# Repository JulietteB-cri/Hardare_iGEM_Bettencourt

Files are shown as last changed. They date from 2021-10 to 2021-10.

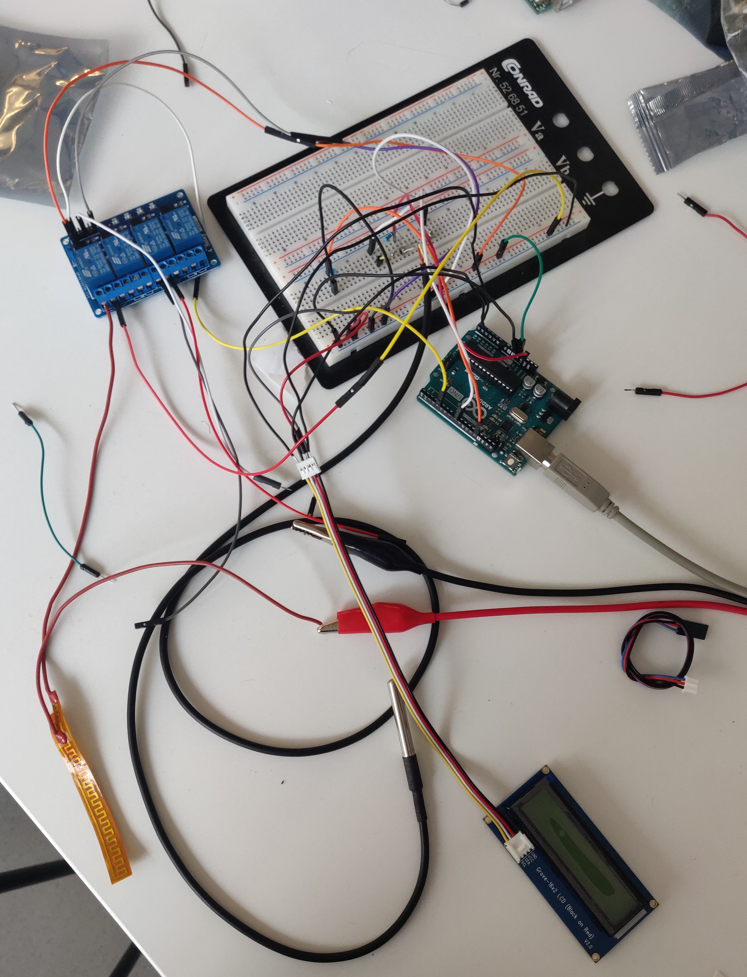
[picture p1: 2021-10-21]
Pictures/Firsts Drafts/IMG_20210827_180004.jpg

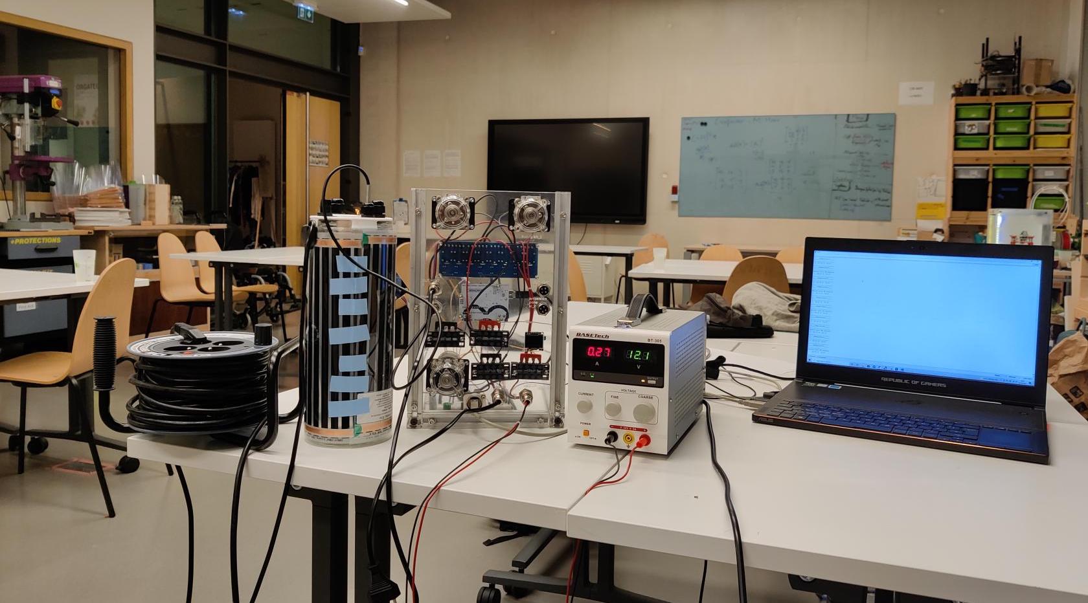
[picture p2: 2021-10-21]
Pictures/IMG_20211005_224018.jpg

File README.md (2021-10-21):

# Hardare_iGEM_Bettencourt

Here is the repository for all the documentation on the Hardware design of Paris Bettencourt team 

Members of this project: 
- Michael Sedbon
- Daria Fedorova
- Sarah Haggenmüller
- Etienne Lemiere
- Nathália Raquel de Souza Fernandes
- Juliette Bellengier

We wished to create our bioreactor to automatize our biological process and increase the biosafety.

# Working principle

To meet the objective described above, we produced a prototype version of the bioreactors system, testing parts and principles. We present here a working proof of concept with a breakdown of the components used as well as ideas to improve some of the parts and the general working principle of the system.

A complete bill of material can be found here 
The Arduino script can be downloaded here
The TouchDesigner network running the Graphical User Interface can be downloaded here.

The actual version of the working prototype consists of two tanks
- One, growing the bacterial culture 
- The second aimed to separate minicells from mother cells and to start pigment production through inputs of chemical cue (Arabinose)

Each tank is temperature-controlled with separated heating systems and thermometers.
Stirring and aeration of the two tanks are achieved through individually controlled peristaltic pumps.
Transfer from the growth tank to the minicell expression tank is handled by a peristaltic pump.
Filtering of the minicells has not been considered for this proof of concept but some research has been done regarding the filtering mechanism to be used.
Control of the system is handled through a single Arduino Uno. 
High voltage devices (Peristaltic pump and heating mats) are switched through relays.

## Overall design 

### 3D Printed lid 

**For the growth thank**

The optical density (OD) sensor is held on a floating 3D printed tube allowing the sensor to always sit right at the surface of the culture
4 holes were placed on the lid to fit cable glands holding stainless steel tubing.
A 4mm internal diameter (ID) stainless steel tube is maintaining the temperature sensor in place (hence always measuring temperature from the same location).

The 3, 8mm ID stainless steel tubes are carrying stirring through bubbling and liquid handling from one tank to the other.

**For the Pigment production tank**

The design of the lid for the pigment production tank is similar to the one of the growth tank except that optical density is not measured here, hence, the mechanism holding the OD sensor has been removed.

Here, stainless steel tubes were used as they were readily available but Polyvinyl chloride (PVC) tubes might be considered to lower the costs

## Laser cutted Panel

A panel holding all the electronic components (Arduino, peristaltic pumps, relays, power and sensor connectors) was designed and laser cut out of 3mm thick transparent Acrylic. 
The panel was mounted on 20x20mm V slot aluminum extrusion
This setup allows for fast and clean prototyping, scalability while keeping costs minimal.
3mm Acrylic proved to be slightly too fragile and other laser cuttable materials might be considered. Another alternative would be to stiffen the V Slot aluminum profile construction to have as little weight as possible on the acrylic panel.
The DXF file for laser cutting the panel can be found here

## Heating mats

### What and why

Two off the shelf heating pads were purchased from a pet shop (These heating pads were originally designed to be used in terrariums for maintaining the required temperature for reptiles).
These mats were wrapped around both tanks and hooked up to individual channels of the relay.
This setup proved to reach the required temperature (up to 42*c from 21*c ambient room temperature).
Future improvements
Two key learning points were extracted from experimenting with this setup:
Even if the required temperature is ultimately achieved, this process remains slow (up to 3 hours)
As we used relays to control the heating pads, the only available control mechanisms were through thresholding at specific temperatures. This process is hard to tune and does not encompass the inertia of the system (even if turned off, the pad remain hot for some times) and only allow for binary values (on or off)

To approach these problems we propose to replace the heating pads with Peletier Elements (allowing to heat the tank faster). The trade-off for such change is that a special frame holding several Peletier elements as well as heatsink systems will need to be designed, hence increasing cost and rendering the entire setup heavier and harder to build. Such change should, therefore, only be considered for use cases where heating faster is required.

To improve control of the temperature, a Mosfet-based system should be considered to allow for non-binary switching of the heating mat (Using a Mosfet-based system would allow to turn on the heating pad at any arbitrarily defined temperature).
With an analog temperature control system, a proper proportional–integral–derivative (PID) controller could be implemented in the control firmware

## Temperature sensor

### What sensors 

Two (one in each tank) DS18B20 temperature sensors were used.
They were chosen for their temperature range (From -55*c to 125*c ), their price (2€ in a package with stainless steel probe and water proof cabling pre-setup), their availability (available at low cost at most online suppliers and local electronic/hobbyist shop), and their convenience to use (these sensors work on with the One-Wire protocol, and, therefore require less installation).
The sensor and the cable were fit through a 4mm Internal diameter stainless tube to insure stability of the system against shaking, possible transport and to increase overall robustness of the design. 
Optical Density (OD) sensor

### What sensors 

To measure the optical density of the growing bacterial culture (triggering the transfer of fully grown bacterias to the pigment expression tank), the DFRobot Gravity Analog Turbidity Sensor was used.
It has been tested and shows sufficient sensitivity to the changes of turbidity specific to the growth of our bacterial cultures.

## Peristaltic pump

### What pump 

Although the original design was cleverly using gravity as a mean to transfer liquids from one tanks to the other, thus preventing the cost relative to the peristaltic pumps, we decided to use these pumps for the proof of concept version of the bioreactor because the design and implementation of watertight systems required for such setup was judged of secondary importance to the proof of concept.
DIY peristaltic pumps were purchased from Amazon.fr and proved sufficient for liquid handling and stirring through bubbling.

### Future improvements

In the actual setup, the liquid handling and stirring pumps are controlled through individual relays. They are, therefore, unidirectional. Being able to control the direction of the pump would allow for more precise liquid handling and better stirring.
To achieve that, H-Bridge component can be added to the system change the direction of the pumps

## Arduino uno

### What 

Arduino is an open-source electronics platform based on easy-to-use hardware and software that is very popular among DIY communities, as a tool to teach and learn STEAMS as well as in research labs across the globe for its low cost and high flexibility/modularity characteristics. 

We based the control mechanism of our design on an Arduino Uno

## Future improvements (Making a PCB ?)
In its current state, wiring of all the components (The temperature and Optical Density sensors, the relays and the OLED screen displaying real-time data) is done through Jumper cables and breadboards. The design of a custom Printed Circuit board (PCB) in the form of an Arduino shield would greatly help reproduce the setup as much less wiring would be required, thus, preventing human mistakes, saving time and cost in production as well as providing a cleaner workbench.

## Graphical user interface (GUI)

### What (TOUCH_DESIGNER)

We developed a graphical user interface (GUI) that displays the current state of the sensor's measurement, of the relays controlling the pumps and the recorded data.

It offers the possibility to overwrite the automated program and to manually control the liquid handling pump (for example to extract liquid from the growth tank in order to perform some measurement).

The software also comes with a Python Base Data Logger recording the state of the system at a customisable rate on a CSV file.

The GUI also offers the possibility to showcase the recorded data in real time and to load files and instantaneously graph data from previous experiments.

The implementation was based on TouchDesigner, a node based programming environment primarily designed for the interaction design community allowing for extremely fast prototyping through a high level of modularisation.
If a TouchDesigner license has to be purchased for commercial purpose, the GUI has been designed in order to run on the free version of touchdesigner (available both for Windows and MacOS)

## Relays

### What 

We used an 8 channel optocoupler driven 5v Relay array to control the heating mats and the 3 peristaltic pumps. All together, these components takes 5 of the 8 channels leaving some free to hook up other devices (such as other pumps or valves for chemical inputs)

### Future improvements (Using optically driven relay to spare the noise?)
As they get triggered these mechanical relays produce a clicking sound. It is subtle but can be heard and problematic to implement in specific places (such as retail or other sound sensitive environments). As an alternative, Solid State relays might be used.

## OLED Screen

### What 

An SSD 1306 OLED Screen has been mounted on the panel to display the sensor's data in real time. This display has been chosen for its availability (available at low cost in most online suppliers and local electronic/hobbyist shops), its convenience (simple integration with the Adafruit_SSD1306 Library and simple 4 pin wiring) and its price (less than 5€ on amazon).

## Future improvements
Despite its many advantages, this display remains small and with a limited resolution (124x64 px). Reading information might be challenging and another display can be considered.

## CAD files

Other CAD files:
_CAD/HAT_perso.3dm
_CAD/couvercle.3dm
_CAD/couvercle_rhino_6.3dm

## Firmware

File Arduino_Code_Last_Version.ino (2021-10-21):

#include <Arduino.h>
#include <math.h>
#include <OneWire.h>
#include <DallasTemperature.h>

//https://randomnerdtutorials.com/guide-for-oled-display-with-arduino/
//DISPLAY STUFFS

#include <Adafruit_GFX.h>
#include <Adafruit_SSD1306.h>
#include <SPI.h>
#include <Wire.h>

#include <ezOutput.h> // ezOutput library

#define SCREEN_WIDTH 128 // OLED display width, in pixels
#define SCREEN_HEIGHT 64 // OLED display height, in pixels

// Declaration for an SSD1306 display connected to I2C (SDA, SCL pins)
#define OLED_RESET -1 // Reset pin # (or -1 if sharing Arduino reset pin)
Adafruit_SSD1306 display(SCREEN_WIDTH, SCREEN_HEIGHT, &Wire, OLED_RESET);

#define ONE_WIRE_BUS 6

OneWire oneWire(ONE_WIRE_BUS);
DallasTemperature sensors(&oneWire);

float Celcius = 0;
float Fahrenheit = 0;
//https://lastminuteengineers.com/ds18b20-arduino-tutorial/
//Multiple_temperature_sensors

int air_pump1 = 6;
int air_pump2 = 2;
int liquid_handling_pump = 2;

int temperature_threshold_1 = 40;
int temperature_threshold_2 = 35;
int heater_pin1 = 8;
int heater_pin2 = 9;

ezOutput _air_pump1(air_pump1);   // create ezOutput object that attach to pin 7;
ezOutput _air_pump2(air_pump2);   // create ezOutput object that attach to pin 8;
int _bubling_lenght = .5 * 60;    //   in seconds
int _bubling_frequency1 = 5 * 60; // in seconds
int _bubling_frequency2 = 5 * 60; // in seconds

int _state_heater_1 = 0;
int temp1 = 0;

float current_od = 0;

int deviceCount = 0;
float tempC1;
float tempC2 = 0.0;

const int buttonPin = 10; // the number of the pushbutton pin
int buttonState = 0;      // variable for reading the pushbutton status
const int ledPin = 13;    // the number of the LED pin

int incomingByte = 0; // for incoming serial data

bool enable_screen = false;

bool Heaters_overritte = false;

void display_variable_on_screen()
{
  display.clearDisplay();
  display.setTextSize(1); // Normal 1:1 pixel scale
  //display.setTextColor(WHITE); // Draw white text
  display.setTextColor(BLACK, WHITE);
  display.setCursor(0, 0); // Start at top-left corner
  display.cp437(true);     // Use full 256 char 'Code Page 437' font
  display.print("BIO_REACTOR 1");

  display.setTextSize(1);      // Normal 1:1 pixel scale
  display.setTextColor(WHITE); // Draw white text

  display.setCursor(10, 10); // Start at top-left corner
  //String temperature1 = "Temp1 = " + String(temp1) + " *C";
  String temperature1 = "Temp1 = ";
  display.print(temperature1);

  display.setCursor(60, 10); // Start at top-left corner
  display.print(tempC1);

  display.setCursor(0, 40); // Start at top-left corner
  String _s_OD = "OD = ";
  display.print(current_od);

  display.display();
}

void int_test_screen()
{

  display.clearDisplay();

  display.setTextSize(1);      // Normal 1:1 pixel scale
  display.setTextColor(WHITE); // Draw white text
  display.setCursor(0, 0);     // Start at top-left corner
  display.cp437(true);         // Use full 256 char 'Code Page 437' font

  for (int16_t i = 0; i < 256; i++)
  {
    if (i == '\n')
      display.write(' ');
    else
      display.write(i);
  }

  display.display();
}

int read_temperature(bool debug = false, bool verbose = false)
{
  if (verbose)
  {
    Serial.println("_____________________");
    Serial.println("_____Temperature_____");
    Serial.println("_____________________");
  }

  sensors.requestTemperatures();
  Celcius = sensors.getTempCByIndex(0);
  Fahrenheit = sensors.toFahrenheit(Celcius);
  if (debug)
  {
    Serial.print(" C ");
    Serial.print(Celcius);
    // Serial.print(" F  ");
    // Serial.println(Fahrenheit);
    // delay(1000);
  }

  if (verbose)
  {
    Serial.print(" C ");
    Serial.print(Celcius);

    Serial.println("_____________________");
    Serial.println("_____Temperature_____");
    Serial.println("_____________________");
  }

  return Celcius;
}

void read_multiple_temperature_sensors()
{
  // bool data1_is_valid = false;
  // bool data2_is_valid = false;
  // Send command to all the sensors for temperature conversion
  sensors.requestTemperatures();

  // Display temperature from each sensor
  //https://lastminuteengineers.com/multiple-ds18b20-arduino-tutorial/
  for (int i = 0; i < deviceCount; i++)
  {
    if (i == 0)
    {
      
      Serial.print("Sensor ");
      Serial.print(i + 1);
      Serial.print(" : ");
      tempC2 = sensors.getTempCByIndex(i);
      Serial.print(tempC2);
      Serial.print("C  |  ");
     
    }
    else if (i == 1)
    {
      
      Serial.print("Sensor ");
      Serial.print(i + 1);
      Serial.print(" : ");
      //tempC2 = sensors.getTempCByIndex(i);
      tempC1 = sensors.getTempCByIndex(i);
      Serial.print(tempC1);
      //Serial.print(tempC2);
      //Serial.print((char)176);//shows degrees character
      Serial.println("C  |  ");
      
    }
  }
}

float readOD(bool verbose = false)
{
  if (verbose)
  {
    Serial.println("_____________________");
    Serial.println("_____OD_____");
    Serial.println("_____________________");
  }
  int sensorValue = analogRead(A0);             // read the input on analog pin 0:
  float voltage = sensorValue * (5.0 / 1024.0); // Convert the analog reading (which goes from 0 - 1023) to a voltage (0 - 5V):
  Serial.println(voltage);                      // print out the value you read:
  //delay(500);
  if (verbose)
  {
    Serial.println("_____________________");
    Serial.println("_____OD_____");
    Serial.println("_____________________");
  }
  return voltage;
}

void temperateure_sensor_reading1(bool verbose = false)
{
  sensors.requestTemperatures();
  Celcius = sensors.getTempCByIndex(0);
  Fahrenheit = sensors.toFahrenheit(Celcius);
  Serial.print(" C  ");
  Serial.print(Celcius);
  Serial.print(" F  ");
  Serial.println(Fahrenheit);
  //delay(1000);
  temp1 = read_temperature();

  if (temp1 > temperature_threshold_1)
  {
    if (verbose)
    {
      Serial.println("should turn off heater1");
      digitalWrite(heater_pin1, HIGH);
    }

    _state_heater_1 = 1;
  }
  else
  {
    if (verbose)
    {
      Serial.println("should turn ON heater1");
      digitalWrite(heater_pin1, LOW);
    }

    _state_heater_1 = 0;
  }

  digitalWrite(heater_pin1, _state_heater_1);
}

void hande_bubling()
{
  _air_pump1.loop(); // MUST call the led1.loop() function in loop()
  _air_pump2.loop(); // MUST call the led2.loop() function in loop()
}

void handle_liquid_handlingg()
{
  //Need to define when we move culture fron Bio_reactor1 to Bio_reactor2

  /*
  digitalWrite(liquid_handling_pump, HIGH);
  digitalWrite(liquid_handling_pump, LOW);
  */
}

void handle_serial_receive()
{
  if (Serial.available() > 0)
  {
    // read the incoming byte:
    incomingByte = Serial.read();

    // prints the received data
    Serial.print("I received: ");
    char message = (char)incomingByte;
    //Serial.println(message);
    if (message == 'p')
    {
      Serial.println("SHOULD ACTIVATE PUMP");
      digitalWrite(ledPin, HIGH);
      Serial.println("button up");
      digitalWrite(liquid_handling_pump, LOW);
    }

    //HEATERS STUFFFS
    if (message == 'h')
    {
      Serial.println("Should_over_wire_heaters");
      Heaters_overritte = true;
    }
    if (message == 'u')
    {
      Serial.println("Heaters_back_to_normal");
      Heaters_overritte = false;
    }

    if (message == '0')
    {
      Serial.println("should_turn_On_heater1");
      digitalWrite(heater_pin1, LOW);
      
    }

    if (message == '1')
    {
      Serial.println("should_turn_off_heater1");
      digitalWrite(heater_pin1, HIGH);
      
    }

    if (message == '2')
    {
      Serial.println("should_turn_On_heater2");
      digitalWrite(heater_pin2, LOW);
      
    }

    if (message == '3')
    {
      Serial.println("should_turn_off_heater2");
      digitalWrite(heater_pin2, HIGH);
      
    }
  //HEATERS STUFFFS

    else if (message == 'v')
    {
      Serial.println("SHOULD DEACTIVATE PUMP");
      digitalWrite(ledPin, LOW);
      Serial.println("button up");
      digitalWrite(liquid_handling_pump, HIGH);
    }
  }
}

void handle_heaters(bool debug = false)
{

  if (tempC1 < temperature_threshold_1)
  {
    digitalWrite(heater_pin1, LOW);
    if (debug)
    {
      Serial.println("HEATER1 IS ON");
    }
  }
  else
  {
    digitalWrite(heater_pin1, HIGH);
    if (debug)
    {
      Serial.println("HEATER1 IS OFF");
    }
  }

  //////////////////////////////

  if (tempC2 < temperature_threshold_2)
  {
    digitalWrite(heater_pin2, LOW);
    if (debug)
    {
      Serial.println("HEATER2 IS ON");
    }
  }
  else
  {
    digitalWrite(heater_pin2, HIGH);
    if (debug)
    {
      Serial.println("HEATER2 IS OFF");
    }
  }
}

void handle_button()
{
  buttonState = digitalRead(buttonPin);

  // check if the pushbutton is pressed. If it is, the buttonState is HIGH:
  if (buttonState == HIGH)
  {
    // turn LED on:
    digitalWrite(ledPin, HIGH);
    Serial.println("button up");
    digitalWrite(liquid_handling_pump, LOW);
  }
  else
  {
    // turn LED off:
    digitalWrite(ledPin, LOW);
    digitalWrite(liquid_handling_pump, HIGH);
  }
}

void log_data()
{
  String Data_to_log = "d,";
  int air_pump1_state = digitalRead(air_pump1);
  int air_pump2_state = digitalRead(air_pump2);
  int air_pump_Liquid_handling_state = digitalRead(liquid_handling_pump);

  Data_to_log = "d," + String(tempC1) + "," + String(tempC2) + "," + String(temperature_threshold_1) + "," + String(temperature_threshold_2) + "," + String(current_od) + "," + String(air_pump1_state) + "," + String(air_pump2_state) + "," + String(air_pump_Liquid_handling_state);

  Serial.println(Data_to_log);
}

void log_data2()
{
  //temperature1,temperature2,temp_treshold1,temp_treshold2,OD,Air_pump1_state,Air_pump2_state,Liquid_handling_pump_state
  int air_pump1_state = 1 - digitalRead(air_pump1);
  int air_pump2_state = 1 - digitalRead(air_pump2);
  int air_pump_Liquid_handling_state = 1 - digitalRead(liquid_handling_pump);

  int heater1_state = 1 - digitalRead(heater_pin1);
  int heater2_state = 1 - digitalRead(heater_pin2);

  Serial.println("");
  Serial.print("d,");
  Serial.print(tempC1);
  Serial.print(",");
  Serial.print(tempC2);
  Serial.print(",");
  Serial.print(temperature_threshold_1);
  Serial.print(",");
  Serial.print(temperature_threshold_2);
  Serial.print(",");
  Serial.print(current_od);
  Serial.print(",");
  Serial.print(air_pump1_state);
  Serial.print(",");
  Serial.print(air_pump2_state);
  Serial.print(",");
  Serial.print(air_pump_Liquid_handling_state);

  Serial.print(",");
  Serial.print(heater1_state);
  Serial.print(",");
  Serial.print(heater2_state);

  Serial.println("");
}
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

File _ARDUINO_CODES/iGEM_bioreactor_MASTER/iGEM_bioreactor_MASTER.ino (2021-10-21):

#include <OneWire.h>
#include <DallasTemperature.h>

#define ONE_WIRE_BUS 6

OneWire oneWire(ONE_WIRE_BUS);
DallasTemperature sensors(&oneWire);

float Celcius=0;
float Fahrenheit=0;
//https://lastminuteengineers.com/ds18b20-arduino-tutorial/

int air_pump1 = 3;
int air_pump2 =2;
int liquid_handling_pump = 5;

int temperature_threshold_1 = 26;
int heater_pin1 = 8;
int heater_pin2 = 9;

void setup() {
  // put your setup code here, to run once:

  Serial.begin(9600); //Baud rate: 9600

  Serial.println("_____________________");
  Serial.println("_____Hello Wolrd_____");
  Serial.println("_____________________");

  sensors.begin();
  
  pinMode(air_pump1, OUTPUT);
  pinMode(air_pump2, OUTPUT);
  pinMode(liquid_handling_pump, OUTPUT);

  pinMode(heater_pin1, OUTPUT);
  pinMode(heater_pin2, OUTPUT);
}


int read_temperature(){
  Serial.println("_____________________");
  Serial.println("_____Temperature_____");
  Serial.println("_____________________");
  
  sensors.requestTemperatures(); 
  Celcius=sensors.getTempCByIndex(0);
  Fahrenheit=sensors.toFahrenheit(Celcius);
  Serial.print(" C  ");
  Serial.print(Celcius);
  Serial.print(" F  ");
  Serial.println(Fahrenheit);
  delay(1000);

  Serial.println("_____________________");
  Serial.println("_____Temperature_____");
  Serial.println("_____________________");

  return Celcius;
} 

float readOD(){
  Serial.println("_____________________");
  Serial.println("_____OD_____");
  Serial.println("_____________________");

  int sensorValue = analogRead(A0);// read the input on analog pin 0:
  float voltage = sensorValue * (5.0 / 1024.0); // Convert the analog reading (which goes from 0 - 1023) to a voltage (0 - 5V):
  Serial.println(voltage); // print out the value you read:
  delay(500);
  Serial.println("_____________________");
  Serial.println("_____OD_____");
  Serial.println("_____________________");
  return voltage;
}

void loop() {
  // put your main code here, to run repeatedly:

  digitalWrite(air_pump1, HIGH);
  digitalWrite(air_pump2, HIGH);
  digitalWrite(liquid_handling_pump, HIGH);
/*
  digitalWrite(air_pump1, HIGH);
  digitalWrite(air_pump2, HIGH);
  digitalWrite(liquid_handling_pump, HIGH);

  delay(1000);
  
  digitalWrite(air_pump1, LOW);
  digitalWrite(air_pump2, LOW);
  digitalWrite(liquid_handling_pump, LOW);
  delay(1000);
*/
  sensors.requestTemperatures(); 
  Celcius=sensors.getTempCByIndex(0);
  Fahrenheit=sensors.toFahrenheit(Celcius);
  Serial.print(" C  ");
  Serial.print(Celcius);
  Serial.print(" F  ");
  Serial.println(Fahrenheit);
  delay(1000);
  int temp1 = read_temperature();

  if  (temp1 > temperature_threshold_1){
    Serial.println("should turn off heater1");
    digitalWrite(heater_pin1,HIGH);
  }else{
    Serial.println("should turn ON heater1");
    digitalWrite(heater_pin1,LOW);
  }

}
  
  

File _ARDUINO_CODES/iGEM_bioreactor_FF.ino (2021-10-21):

#include <FlowMeter.h>
#include <OneWire.h>
#include <DallasTemperature.h>
#include <Wire.h>
#include "rgb_lcd.h"


////////////////////////////////////////////////////////////Variables////////////////////////////////////////////////////////////
rgb_lcd lcd;

OneWire oneWire(8); //ONE_WIRE_BUS
DallasTemperature temperature_sensor(&oneWire);

FlowMeter *Meter;
int period = 1000; //time to get a flowrate in ms

struct sensors_value { 
  float Temperature;
  float OD;
  float Water_Flow = 0;
} sensors; //Structure for storing all the sensors values. You can access it with sensors.Temperature, sensors.OD...

bool pump_working = false;
int millis_start = 0;


////////////////////////////////////////////////////////////Execution Code////////////////////////////////////////////////////////////
void setup() {
  temperature_sensor.begin();
  Serial.begin(9600);
  pinMode(4,OUTPUT); //Heating system
  pinMode(13,OUTPUT); //LED
  pinMode(8, INPUT); //Temp reception
  pinMode(A2, INPUT); //Valve control
  pinMode(6, INPUT); //Turbidity control
  pinMode(2,OUTPUT); //AirPump
  

  Meter = new FlowMeter(digitalPinToInterrupt(10), UncalibratedSensor, MeterISR, RISING);

  lcd.begin(16,2); 
  lcd.setRGB(255,0,0);


}

void loop() {
  sensors = ReadSensors();
  run_output();
  update_LCD();
}
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
